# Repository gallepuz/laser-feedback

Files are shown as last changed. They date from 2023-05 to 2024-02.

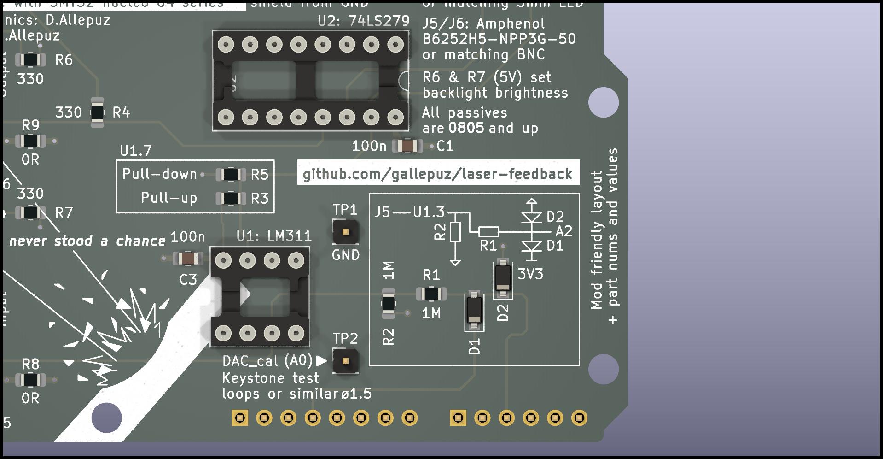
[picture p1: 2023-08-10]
hardware/proto/pulse_generator_shield/clamping schematic.jpg

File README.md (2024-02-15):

# laser-feedback
Lab friendly Arduino/Nucleo shield for interfacing and feedback control of a pulsed laser ablator. It can be used in any application where a pulse's duration must be determined by an independent signal stemming from the subject that is recieving the pulse. 

IMG_2066 (1)

### Build
The complete assembly requires procuring the following:
* PCB populated with components (we have spare unpopulated boards, [contact us](https://twitter.com/uSD_cardlord)!)
* Front panel (we also have spares, in black and green!)
* STM32 nucleo board, we used [this one](https://no.rs-online.com/web/p/microcontroller-development-tools/8644009?cm_mmc=NO-PLA-DS3A-_-google-_-CSS_NO_EN_Pmax_Test-_--_-8644009&matchtype=&&gad_source=1&gclid=Cj0KCQiA5rGuBhCnARIsAN11vgTcTMmP5npaGDRg-D278EnYeHQQxJDi09af2U7zakMZlYZ7tpOIE30aAnx8EALw_wcB&gclsrc=aw.ds)
* [Extruded aluminum enclosure](https://no.rs-online.com/web/p/general-purpose-enclosures/7732981/?redirect-relevancy-data=7365617263685F636173636164655F6F726465723D31267365617263685F696E746572666163655F6E616D653D4931384E525353746F636B4E756D626572267365617263685F6D617463685F6D6F64653D6D61746368616C6C267365617263685F7061747465726E5F6D6174636865643D5E2828282872737C5253295B205D3F293F285C647B337D5B5C2D5C735D3F5C647B332C347D5B705061415D3F29297C283235285C647B387D7C5C647B317D5C2D5C647B377D29292924267365617263685F747970653D52535F53544F434B5F4E554D424552267365617263685F77696C645F63617264696E675F6D6F64653D4E4F4E45267365617263685F6B6579776F72643D3737332D32393831267365617263685F6B6579776F72645F6170703D3737333239383126)
* 3x 11mm long M3 [standoffs](https://no.rs-online.com/web/p/standoffs/1768393/?redirect-relevancy-data=7365617263685F636173636164655F6F726465723D31267365617263685F696E746572666163655F6E616D653D4931384E525353746F636B4E756D626572267365617263685F6D617463685F6D6F64653D6D61746368616C6C267365617263685F7061747465726E5F6D6174636865643D5E2828282872737C5253295B205D3F293F285C647B337D5B5C2D5C735D3F5C647B332C347D5B705061415D3F29297C283235285C647B387D7C5C647B317D5C2D5C647B377D29292924267365617263685F747970653D52535F53544F434B5F4E554D424552267365617263685F77696C645F63617264696E675F6D6F64653D4E4F4E45267365617263685F6B6579776F72643D3137362D38333933267365617263685F6B6579776F72645F6170703D3137363833393326) preferably nylon but these were in stock back then...
* 6x 5mm long M3 [screws](https://no.rs-online.com/web/p/machine-screws/1854400/?redirect-relevancy-data=7365617263685F636173636164655F6F726465723D31267365617263685F696E746572666163655F6E616D653D4931384E525353746F636B4E756D626572267365617263685F6D617463685F6D6F64653D6D61746368616C6C267365617263685F7061747465726E5F6D6174636865643D5E2828282872737C5253295B205D3F293F285C647B337D5B5C2D5C735D3F5C647B332C347D5B705061415D3F29297C283235285C647B387D7C5C647B317D5C2D5C647B377D29292924267365617263685F747970653D52535F53544F434B5F4E554D424552267365617263685F77696C645F63617264696E675F6D6F64653D4E4F4E45267365617263685F6B6579776F72643D3138352D34343030267365617263685F6B6579776F72645F6170703D3138353434303026)
* [Optional] 1x [16 pin DIP socket](https://no.rs-online.com/web/p/dil-sockets/0813137)
* [Optional] 1x [8 pin DIP socket](https://no.rs-online.com/web/p/dil-sockets/0813115)
---

### Use
The output is active high by design and cannot be changed to active low.
1. Connect the artifact to your computer using a USB A to mini B. The front panel backlight will come on. Do not press "ARM". The "Pulse active" and "Arm" LEDs should both be off.
2. Open a USB serial port and set the baud rate to 38400. Adjust the comparator cutoff value and send other configuration commands (need to add more details on this).
3. Connect your setup to the input and output. 
4. Press the square ARM button to enable the output.

**To disarm** the output you need to power cycle the device or press the reset button. Once it is armed it cannot be disarmed. This is by design of the output enable safety failsafe.

---

### Output enable failsafe
Working with lasers can be dangerous, [specially if you cannot see them](https://en.wikipedia.org/wiki/Laser_safety#Safety_measures). So we put effort into designing in a simple circuit that will prevent the device from driving whatever is connected to the output unless it is manually armed by the user first. We achieve this by floating the output with the help of a relay and a spare latch on the 74LS279. With the help of pull resistors and two NPNs we also implement a simple mechanism that prevents the user from arming if the output is high at that time. 

This circuit is thus not controlled by software and will act the same way upon power up every time. 



---

### DTU unit notes
The unit at DTU does not have an identifier at the moment. Its enclosure is not grounded so the green and yellow post is effectively floating.

---

### Grounding the enclosure
On the front panel there is a solid copper path between the BNCs and the corner holes can provide an effective faraday cage to the whole assembly. We say *can* because we haven't tested this. The top right and bottom left can be used to ground the enclosure to the electronics within. The plated region around the input and output holes connects to the washer on the BNC connector but not the shield (at least on the BNC in BOM). The binding post can be used to choose where the enclosure is connected and whether it is connected to system ground if desired. Should add pictures... 

To secure grounding of the enclosure unscrew one of the corner panel screws and place a (conductive) washer.  

---

### Disconnecting the BNC shield - enclosure shunt
By default the shielding on the BNC is connected to the *enclosure and system ground* via the plated rings on the front panel screws and R9 and R8 on the PCB respectively.
- To disconnect the shield further, R8 and R9 can be desoldered.
Doing both of these will float the shielding. Do it partially on one or both BNC connectors to get other configurations.

---

### Known issues
- When the diodes are installed the comparator output is forced high. The diodes present in this BOM are ESD diodes rather than rectifier diodes and are likely the culprit. Removing them fixes the problem. We keep in mind this effectively removes overvoltage protection and 3V3 ADC boards might be damaged if there is no proper control over the photodiode signal amplitude.
- The front panel says this is a PLL, it is not. We forgot to remove it after moving away from another idea...

---

### To Do
Add pictures of grounding.
Eventually deixar només els gerbers i un pdf de l'esquematic a la carpeta hardware.
Add more information on serial interface commands.

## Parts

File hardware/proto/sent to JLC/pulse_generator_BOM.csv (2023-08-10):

Comment | Designator | Footprint | JLCPCB Part #（optional）
1N5711 | D1,D2 | D_SOD-123 | C727115
DAC_cal | TP2 | PinHeader_1x01_P2.54mm_Vertical | C238118
SW_Push | SW1 | SW_Tactile_SPST_Angled_PTS645Vx39-2LFS | C266195
LED | D3 | LED_D5.0mm | C3001995
330 | R7,R4,R6 | R_0805_2012Metric_Pad1.20x1.40mm_HandSolder | C2984391
Conn_Coaxial | J5,J6 | BNC_Amphenol_B6252HB-NPP3G-50_Horizontal | C305920
LED | D5,D4 | LED_0805_2012Metric_Pad1.15x1.40mm_HandSolder | C497949
74LS279 | U2 | DIP-16_W7.62mm_Socket_LongPads | C3170693
0 | R8,R9 | R_0805_2012Metric_Pad1.20x1.40mm_HandSolder | C346501
10k | R3,R5 | R_0805_2012Metric_Pad1.20x1.40mm_HandSolder | C84376
LM311 | U1 | DIP-8_W7.62mm_Socket_LongPads | C305904
1M | R1,R2 | R_0805_2012Metric_Pad1.20x1.40mm_HandSolder | C479091
GND_hook | TP1 | PinHeader_1x01_P2.54mm_Vertical | C238118
100n | C3,C1 | C_0805_2012Metric_Pad1.18x1.45mm_HandSolder | C85866

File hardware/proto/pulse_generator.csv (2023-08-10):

Source: | C:\Users\Guillem\Documents\Guillem\personal\Kicad\pulse_generator\pulse_generator\pulse_generator.kicad_sch
Date: | 08-Aug-23 5:58:08 PM
Tool: | Eeschema 7.0.2
Generator: | C:\Program Files\KiCad\7.0\bin\scripting\plugins/bom_csv_grouped_by_value.py
Component Count: | 27
Collated Components:
Item | Qty | Reference(s) | Value | LibPart | Footprint | Datasheet | DNP
1 | 2 | C1, C3 | 100n | Device:C | Capacitor_SMD:C_0805_2012Metric_Pad1.18x1.45mm_HandSolder | ~
2 | 2 | D1, D2 | 1N5711 | Device:D_Schottky | Diode_SMD:D_SOD-123 | ~
3 | 1 | D3 | LED | Device:LED | LED_THT:LED_D5.0mm | ~
4 | 2 | D4, D5 | LED | Device:LED | LED_SMD:LED_0805_2012Metric_Pad1.15x1.40mm_HandSolder | ~
5 | 1 | J1 | Power | Connector_Generic:Conn_01x08 | Connector_PinHeader_2.54mm:PinHeader_1x08_P2.54mm_Vertical | ~
6 | 1 | J2 | Digital/PWM | Connector_Generic:Conn_01x10 | Connector_PinHeader_2.54mm:PinHeader_1x10_P2.54mm_Vertical | ~
7 | 1 | J3 | Analog | Connector_Generic:Conn_01x06 | Connector_PinHeader_2.54mm:PinHeader_1x06_P2.54mm_Vertical | ~
8 | 1 | J4 | Digital/PWM | Connector_Generic:Conn_01x08 | Connector_PinHeader_2.54mm:PinHeader_1x08_P2.54mm_Vertical | ~
9 | 2 | J5, J6 | Conn_Coaxial | Connector:Conn_Coaxial | Connector_Coaxial:BNC_Amphenol_B6252HB-NPP3G-50_Horizontal | ~
10 | 2 | R1, R2 | 1M | Device:R | Resistor_SMD:R_0805_2012Metric_Pad1.20x1.40mm_HandSolder | ~
11 | 1 | R3 | 10k | Device:R | Resistor_SMD:R_0805_2012Metric_Pad1.20x1.40mm_HandSolder | ~
12 | 3 | R4, R6, R7 | 330 | Device:R | Resistor_SMD:R_0805_2012Metric_Pad1.20x1.40mm_HandSolder | ~
13 | 1 | R5 | 10k | Device:R | Resistor_SMD:R_0805_2012Metric_Pad1.20x1.40mm_HandSolder | ~ | DNP
14 | 2 | R8, R9 | 0 | Device:R | Resistor_SMD:R_0805_2012Metric_Pad1.20x1.40mm_HandSolder | ~
15 | 1 | SW1 | SW_Push | Switch:SW_Push | Button_Switch_THT:SW_Tactile_SPST_Angled_PTS645Vx39-2LFS | ~
16 | 1 | TP1 | GND_hook | Connector:TestPoint | Connector_PinHeader_2.54mm:PinHeader_1x01_P2.54mm_Vertical | ~
17 | 1 | TP2 | DAC_cal | Connector:TestPoint | Connector_PinHeader_2.54mm:PinHeader_1x01_P2.54mm_Vertical | ~
18 | 1 | U1 | LM311 | Comparator:LM311 | Package_DIP:DIP-8_W7.62mm_Socket_LongPads | https://www.st.com/resource/en/datasheet/lm311.pdf
19 | 1 | U2 | 74LS279 | comprovat_parts:74LS279 | Package_DIP:DIP-16_W7.62mm_Socket_LongPads

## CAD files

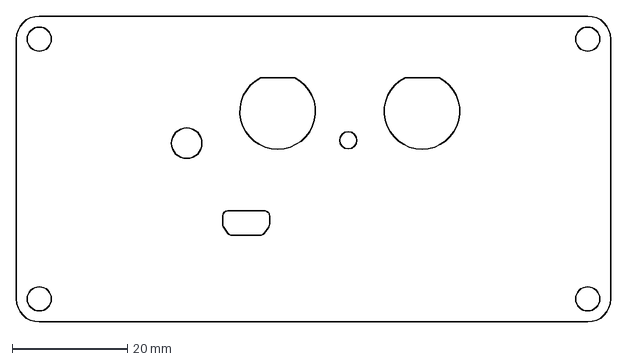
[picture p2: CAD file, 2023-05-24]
hardware/proto/endplate_1455NF.dxf
103.0 x 53.0 mm

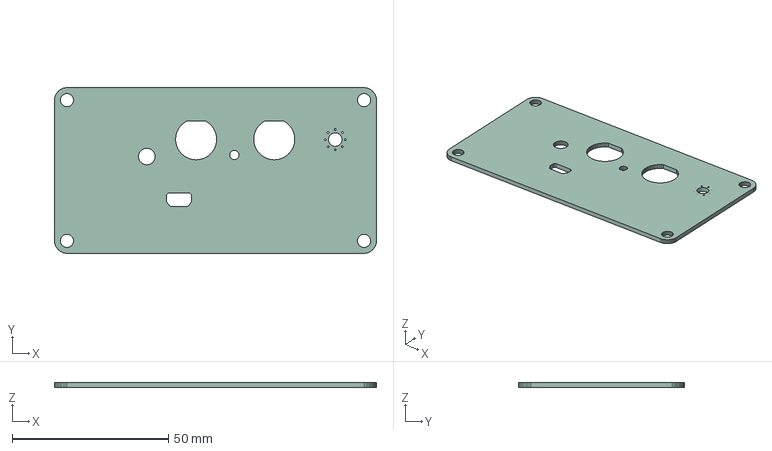
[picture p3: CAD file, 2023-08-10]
hardware/proto/pulse_generator_endplate/pulse_generator_endplate_1455NF.step
103.0 x 53.0 x 1.60 mm

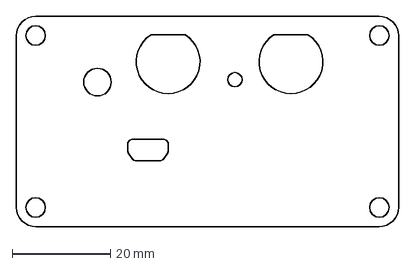
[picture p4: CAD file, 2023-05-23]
hardware/proto/endplate.dxf
77.9 x 42.9 mm

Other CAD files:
hardware/v2/endplate/pulse_generator_endplate_v2.step

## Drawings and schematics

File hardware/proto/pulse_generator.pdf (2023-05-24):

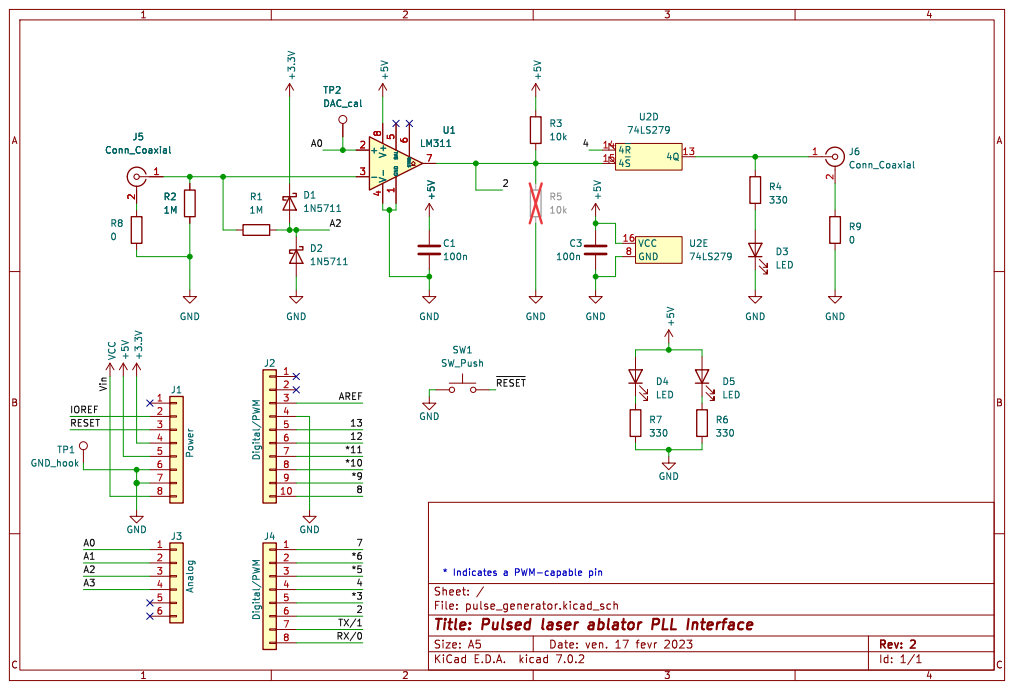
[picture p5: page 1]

Id: 1/1 Title: Pulsed laser ablator PLL Interface

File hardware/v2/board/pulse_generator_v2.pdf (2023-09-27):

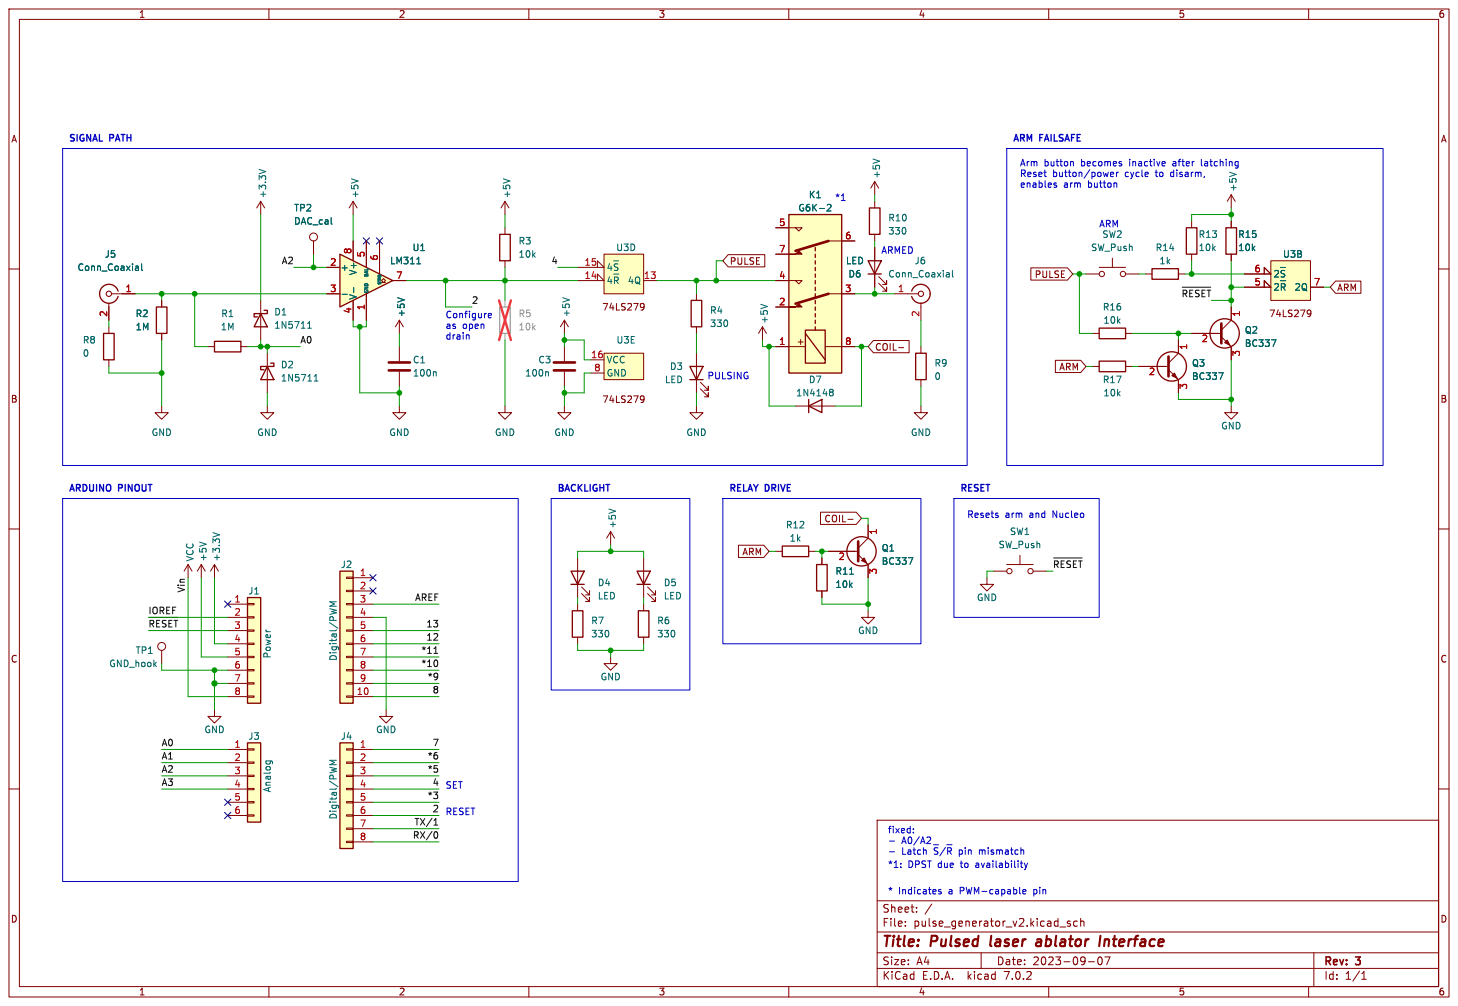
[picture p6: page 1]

Id: 1/1 Title: Pulsed laser ablator Interface

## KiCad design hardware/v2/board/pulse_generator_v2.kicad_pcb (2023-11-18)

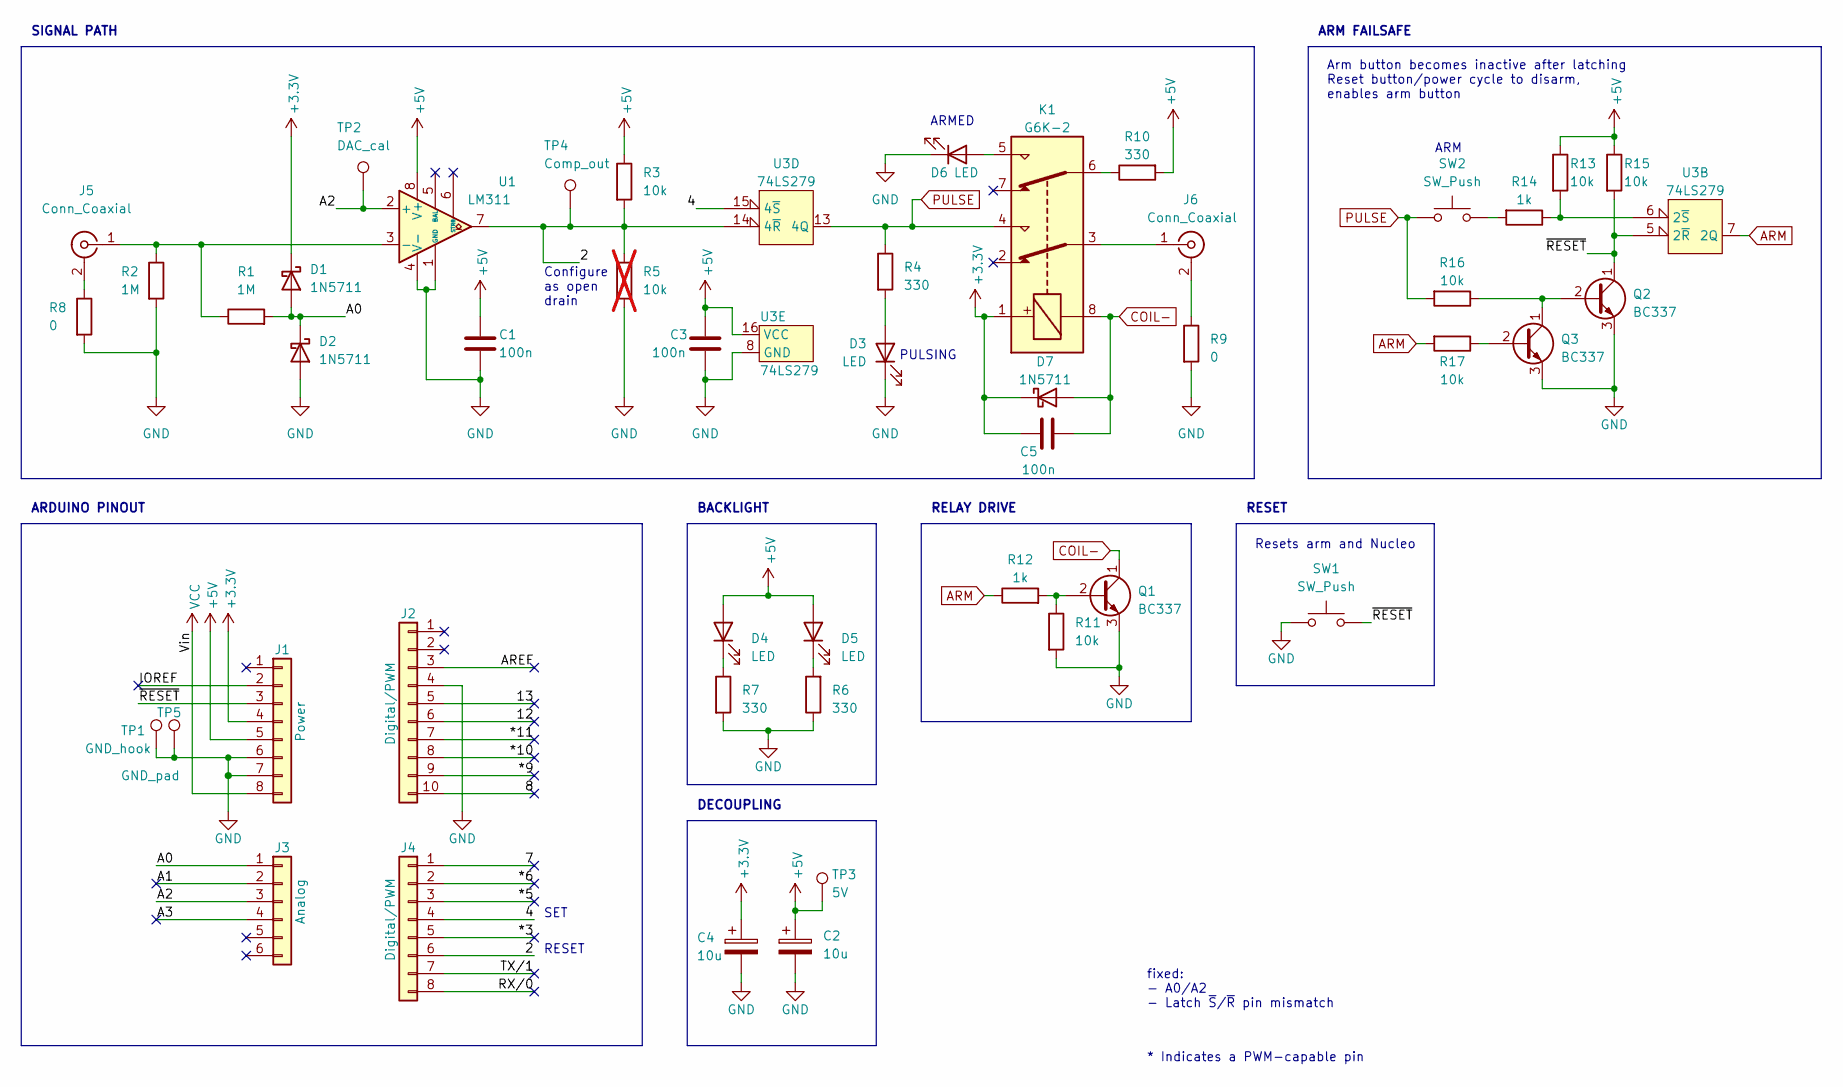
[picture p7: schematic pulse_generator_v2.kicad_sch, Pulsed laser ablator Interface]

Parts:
C1, C3, C5: 100n; C_0805_2012Metric_Pad1.18x1.45mm_HandSolder
C2, C4: 10u; CP_Radial_D5.0mm_P2.50mm
D1, D2, D7: 1N5711; D_SOD-123
D3, D4, D5, D6: LED; LED_D5.0mm
J1: Power; PinHeader_1x08_P2.54mm_Vertical
J2: Digital/PWM; PinHeader_1x10_P2.54mm_Vertical
J3: Analog; PinHeader_1x06_P2.54mm_Vertical
J4: Digital/PWM; PinHeader_1x08_P2.54mm_Vertical
J5, J6: Conn_Coaxial; BNC_Amphenol_B6252HB-NPP3G-50_Horizontal
K1: G6K-2; Relay_DPDT_Omron_G6K-2F-Y
Q1, Q2, Q3: BC337; TO-92_Inline_Wide
R1, R2: 1M; R_0805_2012Metric_Pad1.20x1.40mm_HandSolder
R3, R11, R13, R15, R16, R17: 10k; R_0805_2012Metric_Pad1.20x1.40mm_HandSolder
R4, R6, R7, R10: 330; R_0805_2012Metric_Pad1.20x1.40mm_HandSolder
R5: 10k; R_0805_2012Metric_Pad1.20x1.40mm_HandSolder; not fitted
R8, R9: 0; R_0805_2012Metric_Pad1.20x1.40mm_HandSolder
R12, R14: 1k; R_0805_2012Metric_Pad1.20x1.40mm_HandSolder
SW1, SW2: SW_Push; SW_Tactile_SPST_Angled_PTS645Vx39-2LFS
TP1: GND_hook; PinHeader_1x01_P2.54mm_Vertical
TP2: DAC_cal; PinHeader_1x01_P2.54mm_Vertical
TP3: 5V; PinHeader_1x01_P2.54mm_Vertical
TP4: Comp_out; PinHeader_1x01_P2.54mm_Vertical
TP5: GND_pad; TestPoint_Pad_2.5x2.5mm
U1: LM311; DIP-8_W7.62mm_Socket_LongPads
U3: 74LS279; DIP-16_W7.62mm_Socket_LongPads

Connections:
+3V3: C4.1, C5.1, D1.1 (K), D7.1 (K), J1.4, K1.1
+5V: C1.1, C2.1, C3.1, D4.2 (A), D5.2 (A), J1.5, R3.1, R10.2, R13.1, R15.1, TP3.1, U1.8 (V+), U3.16 (VCC)
/2: J4.6, R3.2, R5.1, TP4.1, U1.7, U3.14 (4~R)
/4: J4.4, U3.15 (4~S)
/7: J4.1
/8: J2.10
/12: J2.6
/13: J2.5
/*3: J4.5
/*5: J4.3
/*6: J4.2
/*9: J2.9
/*10: J2.8
/*11: J2.7
/A0: D1.2 (A), D2.1 (K), J3.1, R1.2
/A1: J3.2
/A2: J3.3, TP2.1, U1.2 (+)
/A3: J3.4
/AREF: J2.3
/IOREF: J1.2
/RX/0: J4.8
/TX/1: J4.7
/~RESET: J1.3, Q2.1 (C), R15.2, SW1.2, U3.5 (2~R)
ARM: R12.1, R17.2, U3.7 (2Q)
COIL-: C5.2, D7.2 (A), K1.8, Q1.1 (C)
GND: C1.2, C2.2, C3.2, C4.2, D2.2 (A), D3.1 (K), D6.1 (K), J1.6, J1.7, J2.4, Q1.3 (E), Q2.3 (E), Q3.3 (E), R2.2, R5.2, R6.1, R7.2, R8.2, R9.2, R11.2, SW1.1, TP1.1, TP5.1, U1.1 (GND), U1.4 (V-), U3.8 (GND)
unnamed: D3.2 (A), R4.2
unnamed: D4.1 (K), R7.1
unnamed: D5.1 (K), R6.2
unnamed: D6.2 (A), K1.5
unnamed: J5.2 (Ext), R8.1
unnamed: J5.1 (In), R1.1, R2.1, U1.3 (-)
unnamed: J6.2 (Ext), R9.1
unnamed: J6.1 (In), K1.3
unnamed: K1.6, R10.1
unnamed: Q1.2 (B), R11.1, R12.2
unnamed: Q2.2 (B), Q3.1 (C), R16.1
unnamed: Q3.2 (B), R17.1
unnamed: R14.2, SW2.2
unnamed: R13.2, R14.1, U3.6 (2~S)
PULSE: K1.4, R4.1, R16.2, SW2.1, U3.13 (4Q)
VCC: J1.8

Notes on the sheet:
ARM
ARMED
SET
DECOUPLING
BACKLIGHT
Configure as open drain
ARDUINO PINOUT
Arm button becomes inactive after latching Reset button/power cycle to disarm, enables arm button
RESET
SIGNAL PATH
ARM FAILSAFE
RELAY DRIVE
fixed: - A0/A2 - Latch ~{S}/~{R} pin mismatch
Resets arm and Nucleo
* Indicates a PWM-capable pin
PULSING

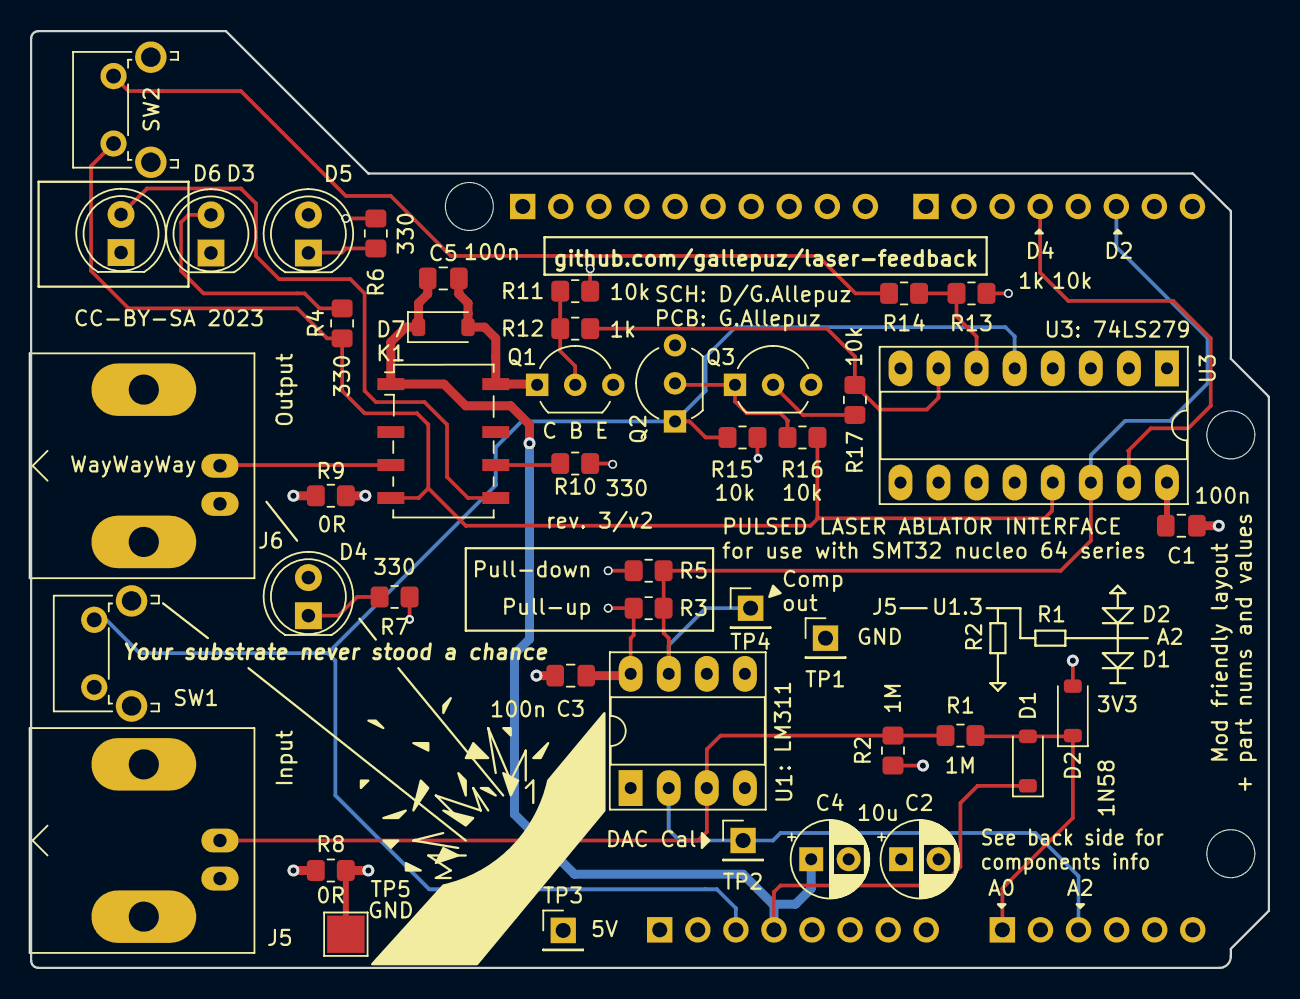
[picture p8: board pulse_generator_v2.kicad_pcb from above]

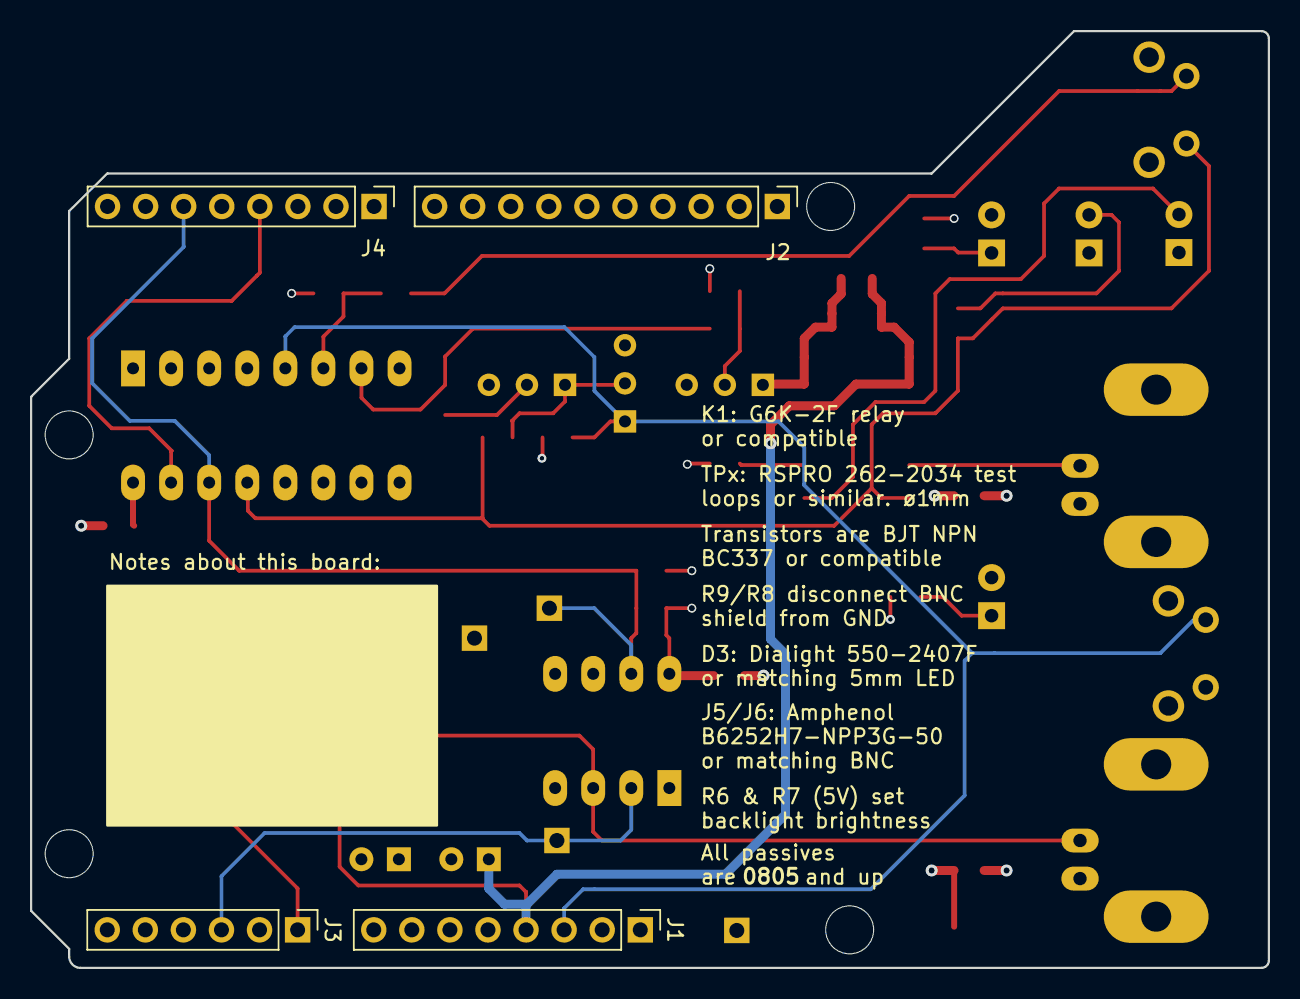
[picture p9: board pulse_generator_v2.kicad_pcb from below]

Board: 4 copper layers, 82.6 x 62.5 mm, 52 parts (4 on the bottom side), 25 nets.

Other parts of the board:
MH1, MH2, MH3, MH4: MountingHole_3.2mm

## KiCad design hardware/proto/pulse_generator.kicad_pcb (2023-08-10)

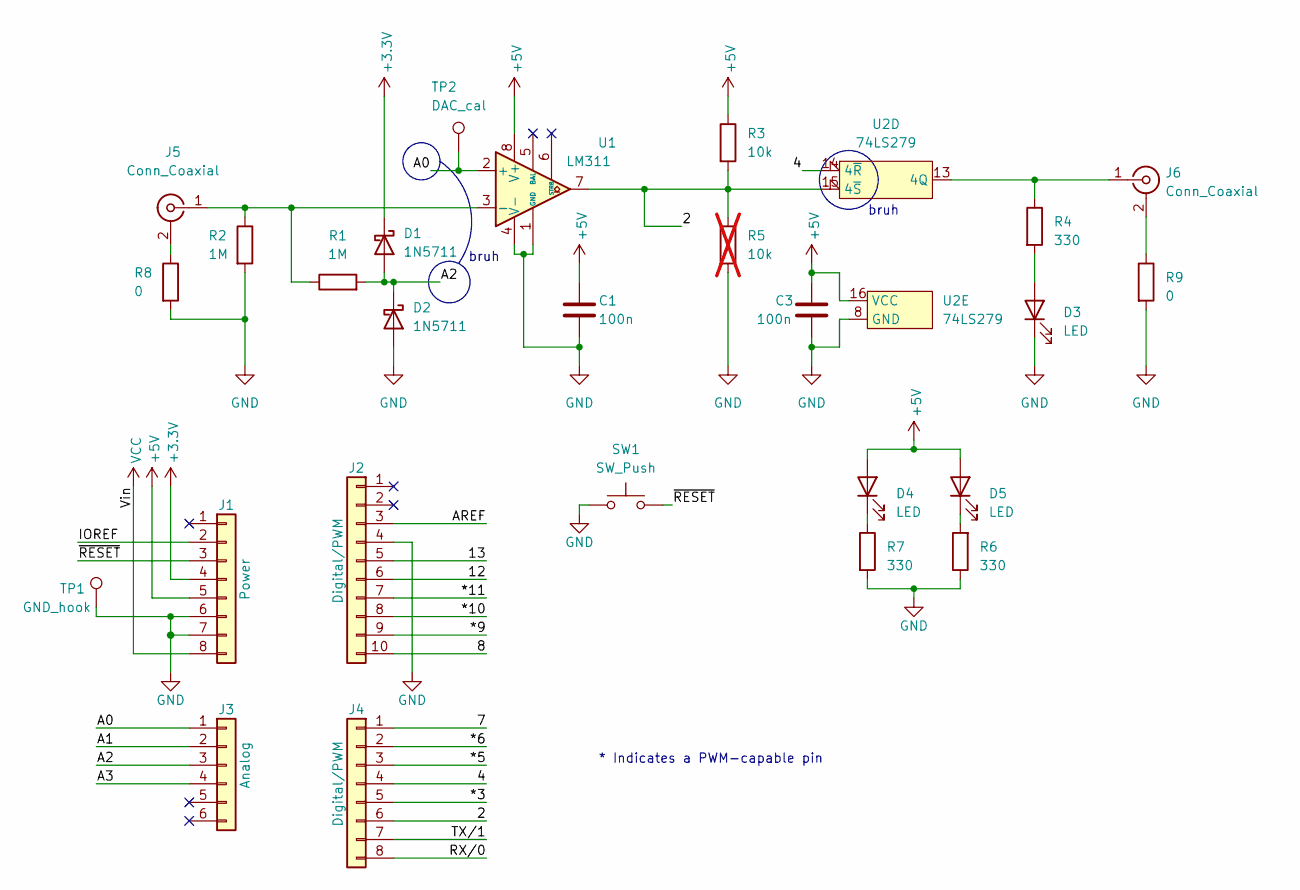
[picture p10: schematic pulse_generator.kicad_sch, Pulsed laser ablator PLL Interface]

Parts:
C1, C3: 100n; C_0805_2012Metric_Pad1.18x1.45mm_HandSolder
D1, D2: 1N5711; D_SOD-123
D3: LED; LED_D5.0mm
D4, D5: LED; LED_0805_2012Metric_Pad1.15x1.40mm_HandSolder
J1: Power; PinHeader_1x08_P2.54mm_Vertical
J2: Digital/PWM; PinHeader_1x10_P2.54mm_Vertical
J3: Analog; PinHeader_1x06_P2.54mm_Vertical
J4: Digital/PWM; PinHeader_1x08_P2.54mm_Vertical
J5, J6: Conn_Coaxial; BNC_Amphenol_B6252HB-NPP3G-50_Horizontal
R1, R2: 1M; R_0805_2012Metric_Pad1.20x1.40mm_HandSolder
R3: 10k; R_0805_2012Metric_Pad1.20x1.40mm_HandSolder
R4, R6, R7: 330; R_0805_2012Metric_Pad1.20x1.40mm_HandSolder
R5: 10k; R_0805_2012Metric_Pad1.20x1.40mm_HandSolder; not fitted
R8, R9: 0; R_0805_2012Metric_Pad1.20x1.40mm_HandSolder
SW1: SW_Push; SW_Tactile_SPST_Angled_PTS645Vx39-2LFS
TP1: GND_hook; PinHeader_1x01_P2.54mm_Vertical
TP2: DAC_cal; PinHeader_1x01_P2.54mm_Vertical
U1: LM311; DIP-8_W7.62mm_Socket_LongPads
U2: 74LS279; DIP-16_W7.62mm_Socket_LongPads

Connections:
+3V3: D1.1 (K), J1.4
+5V: C1.1, C3.1, D4.2 (A), D5.2 (A), J1.5, R3.1, U1.8 (V+), U2.16 (VCC)
/2: J4.6, R3.2, R5.1, U1.7, U2.15 (4~S)
/4: J4.4, U2.14 (4~R)
/7: J4.1
/8: J2.10
/12: J2.6
/13: J2.5
/*3: J4.5
/*5: J4.3
/*6: J4.2
/*9: J2.9
/*10: J2.8
/*11: J2.7
/A0: J3.1, TP2.1, U1.2 (+)
/A1: J3.2
/A2: D1.2 (A), D2.1 (K), J3.3, R1.2
/A3: J3.4
/AREF: J2.3
/IOREF: J1.2
/RX/0: J4.8
/TX/1: J4.7
/~RESET: J1.3, SW1.2
GND: C1.2, C3.2, D2.2 (A), D3.1 (K), J1.6, J1.7, J2.4, R2.2, R5.2, R6.1, R7.2, R8.2, R9.2, SW1.1, TP1.1, U1.1 (GND), U1.4 (V-), U2.8 (GND)
unnamed: D3.2 (A), R4.2
unnamed: D4.1 (K), R7.1
unnamed: D5.1 (K), R6.2
unnamed: J5.2 (Ext), R8.1
unnamed: J5.1 (In), R1.1, R2.1, U1.3 (-)
unnamed: J6.2 (Ext), R9.1
unnamed: J6.1 (In), R4.1, U2.13 (4Q)
VCC: J1.8

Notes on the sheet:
bruh
* Indicates a PWM-capable pin

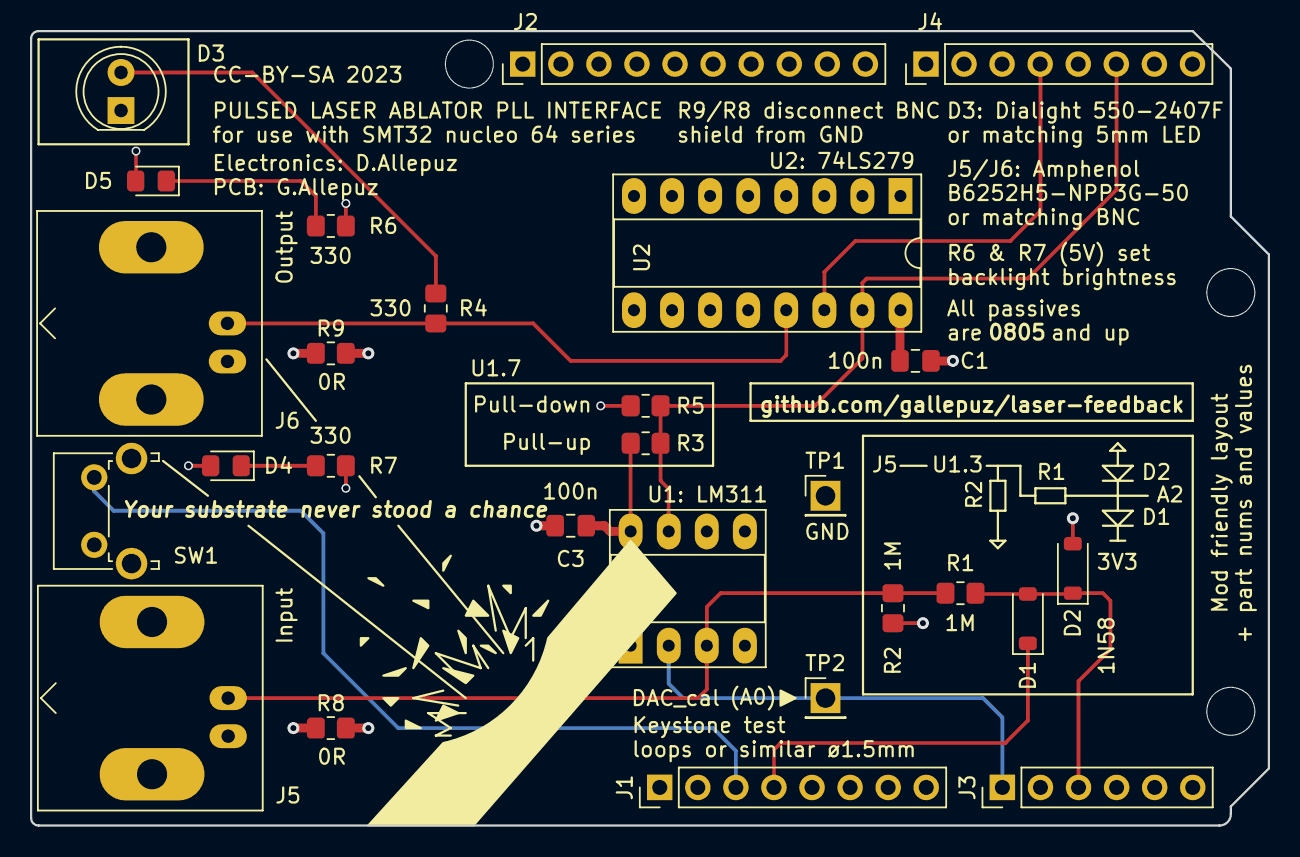
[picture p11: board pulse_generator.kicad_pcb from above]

Board: 4 copper layers, 82.6 x 53.0 mm, 31 parts (0 on the bottom side), 15 nets.

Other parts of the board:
MH1, MH2, MH3, MH4: MountingHole_3.2mm

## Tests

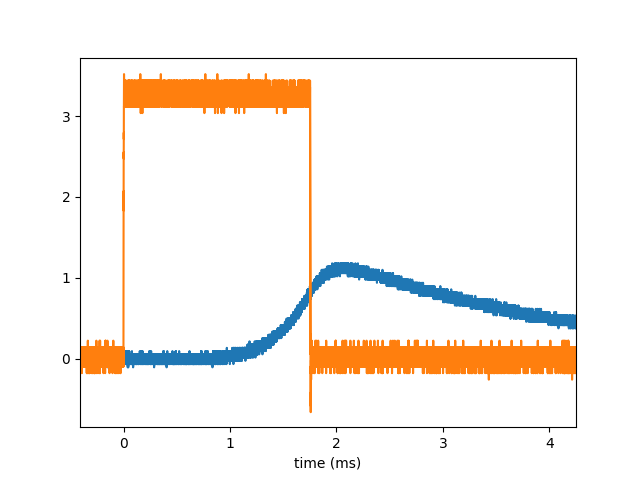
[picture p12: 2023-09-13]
hardware/proto/testing/Figure_1.png

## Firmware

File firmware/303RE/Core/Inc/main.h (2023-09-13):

/* USER CODE BEGIN Header */
/**
  ******************************************************************************
  * @file           : main.h
  * @brief          : Header for main.c file.
  *                   This file contains the common defines of the application.
  ******************************************************************************
  * @attention
  *
  * Copyright (c) 2023 STMicroelectronics.
  * All rights reserved.
  *
  * This software is licensed under terms that can be found in the LICENSE file
  * in the root directory of this software component.
  * If no LICENSE file comes with this software, it is provided AS-IS.
  *
  ******************************************************************************
  */
/* USER CODE END Header */

/* Define to prevent recursive inclusion -------------------------------------*/
#ifndef __MAIN_H
#define __MAIN_H

#ifdef __cplusplus
extern "C" {
#endif

/* Includes ------------------------------------------------------------------*/
#include "stm32f3xx_hal.h"

/* Private includes ----------------------------------------------------------*/
/* USER CODE BEGIN Includes */

/* USER CODE END Includes */

/* Exported types ------------------------------------------------------------*/
/* USER CODE BEGIN ET */
#define SERIAL_TIMEOUT 1000

#define OK		0x01 // ) 0x29
#define FAIL 	0x00 // & 0x26
#define UNKNOWN_COMMAND 0x03 // ' 0x27

// Requests
#define CHECK 			0x00 // ( 0x28 // Send 0x01 always
#define GET_INPUT 		0x01
#define PULSE			0x02 // * 0x2A
#define SET_DAC			0x03 // Receive 4 bytes
#define RST 			0x04
/* USER CODE END ET */

/* Exported constants --------------------------------------------------------*/
/* USER CODE BEGIN EC */

/* USER CODE END EC */

/* Exported macro ------------------------------------------------------------*/
/* USER CODE BEGIN EM */

/* USER CODE END EM */

/* Exported functions prototypes ---------------------------------------------*/
void Error_Handler(void);

/* USER CODE BEGIN EFP */

/* USER CODE END EFP */

/* Private defines -----------------------------------------------------------*/
#define B1_Pin GPIO_PIN_13
#define B1_GPIO_Port GPIOC
#define USART_TX_Pin GPIO_PIN_2
#define USART_TX_GPIO_Port GPIOA
#define USART_RX_Pin GPIO_PIN_3
#define USART_RX_GPIO_Port GPIOA
#define LD2_Pin GPIO_PIN_5
#define LD2_GPIO_Port GPIOA
#define RESET_PULLDOWN_Pin GPIO_PIN_10
#define RESET_PULLDOWN_GPIO_Port GPIOA
#define TMS_Pin GPIO_PIN_13
#define TMS_GPIO_Port GPIOA
#define TCK_Pin GPIO_PIN_14
#define TCK_GPIO_Port GPIOA
#define SWO_Pin GPIO_PIN_3
#define SWO_GPIO_Port GPIOB
#define SET_Pin GPIO_PIN_5
#define SET_GPIO_Port GPIOB

/* USER CODE BEGIN Private defines */

/* USER CODE END Private defines */

#ifdef __cplusplus
}
#endif

#endif /* __MAIN_H */

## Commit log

2023-02-17 untracked files
    [pulse_generator.kicad_pcb, pulse_generator.kicad_sch]
2023-02-18 decoupling lm311 update
    [pulse_generator.kicad_sch]
2023-02-18 wrong comp pd value
    [pulse_generator.kicad_sch]
2023-02-19 sch rev2
    [pulse_generator.kicad_pcb, pulse_generator.kicad_sch]
2023-03-02 guardat amb og shield outline
    [pulse_generator.kicad_pcb]
2023-03-03 shield edge cuts save
    [pulse_generator.kicad_pcb]
2023-03-03 nucleo form factor
    [pulse_generator.kicad_pcb, pulse_generator.kicad_sch]
2023-05-23 Ready for review
    Ready for review
    [pulse_generator.kicad_pcb, pulse_generator.kicad_sch]
2023-05-23 minor tweaks
    [pulse_generator.kicad_pcb]
2023-05-23 Added all assets and 3d models
    [pulse_generator.kicad_pcb]
2023-05-23 past commit failed to add untracked
    [endplate.dxf, laser_feedback_faceplate.kicad_pcb, laser_feedback_faceplate.kicad_sch, pulse_generator_endplate.kicad_pcb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]
2023-05-23 BNC copper padding clearance
    [pulse_generator_endplate.kicad_pcb]
2023-05-24 corrected some stuff, larger enclosure
    [endplate_1455NF.dxf, pulse_generator.kicad_pcb, pulse_generator.kicad_sch, pulse_generator_endplate.kicad_sch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]
2023-05-24 changed "sleeve" for "shield"
    [pulse_generator_endplate_1455NF.kicad_pcb]
2023-05-24 rearrange diode clamp section
    [pulse_generator.kicad_pcb, pulse_generator_endplate_1455NF.kicad_pcb]
2023-08-10 Please enter the commit message for your changes. Lines starting
    [pulse_generator.kicad_pcb, pulse_generator_endplate_1455NF.kicad_pcb]
2023-08-10 obviously fd it
    [endplate.dxf, endplate_1455NF.dxf, laser_feedback_faceplate.kicad_pcb, laser_feedback_faceplate.kicad_sch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]
2023-08-10 added gitignore, firmware, tidy up
    [laser_feedback_faceplate.kicad_pcb, laser_feedback_faceplate.kicad_sch]
2023-09-05 some changes related to testing
    [pulse_generator.kicad_sch]
2023-09-13 moving stuff around
    [endplate.dxf, endplate_1455NF.dxf, pulse_generator-B_Cu.gbr, pulse_generator-B_Fab.gbr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]
2023-09-13 untracked hardware
    [100mm_V1024_trace_0_0_downsampled.csv, 100mm_V1024_trace_0_0_downsampled_newline.csv, endplate.dxf, endplate_1455NF.dxf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]
2023-09-24 added pdf of v2 w relay circuit
    [pulse_generator_v2.kicad_sch]
2023-09-24 added untracked v2 pdf w relay circuit
2023-09-27 failsafe arm fixes
    [pulse_generator_v2.kicad_sch]
2023-10-11 added failsafe arm, mech fixes
    [pulse_generator_v2.kicad_pcb, pulse_generator_v2.kicad_sch]
2023-10-11 v2 hw with failsafe arm and mech fixes
    [pulse_generator_endplate_v2.kicad_pcb, pulse_generator_endplate_v2.kicad_sch, pulse_generator_endplate_v2.step, pulse_generator_v2.kicad_pcb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]
2023-10-12 gerbers out
    [pulse_generator_endplate_v2.kicad_pcb, pulse_generator_v2.kicad_pcb, pulse_generator_v2.kicad_sch]
2023-11-18 first commit after final at DTU
    [pulse_generator_endplate_v2-B_Cu.gbr, pulse_generator_endplate_v2-B_Mask.gbr, pulse_generator_endplate_v2-B_Silkscreen.gbr, pulse_generator_endplate_v2-Edge_Cu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]
2024-02-15 Added use section and safety circuit explanation

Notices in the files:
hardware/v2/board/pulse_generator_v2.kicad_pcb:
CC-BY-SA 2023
